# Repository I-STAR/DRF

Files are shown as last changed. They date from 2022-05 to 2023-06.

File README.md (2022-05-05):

# Open Source Library of Dynamic Reference Frames

It can be difficult to find commercially available dynamic reference frames (DRFs) for surgical tracking/navigation with a large diversity of designs permitting simultaneous tracking. As a result, many researchers resort to building their own custom-built tools. The purpose of this open-source library is to provide a variety of sets of mutually-compatible DRFs ready for 3D printing and freely available to the research community.

Please enjoy the fruits of our labor with this library of 10 sets:

- APPLE
- BANANA
- CHERRY
- DATE
- EGGFRUIT
- FIG
- GUAVA
- HONEYDEW
- JUJUBE
- KIWI

of mutually compatible dynamic reference frames (DRFs) with passive, retro-reflective markers. The APPLE set contains 10 tools, while the others contain 6. The first tool in each of the sets is the same, similar to NDI reference tool (#8700339).

The library was designed and validated at I-STAR Lab at Johns Hopkins University. All DRFs were constructed and validated using Northern Digital Inc. (NDI) geometry specifications.

# Usage Instructions

Below is a step-by-step guide to tracking DRFs with any NDI tracking system (such as Polaris Vicra or Spectra).

**STEP 1**: Download a DRF set(s) of your choosing along with the mounting post.

**STEP 2**: If you wish to modify the DRF in any way (e.g., change name, add/remove a clearance hole), use the [OpenSCAD][scad] program to open and edit the .scad file. Save by clicking “render” and then “export as STL.”

**STEP 3**: Once you have the STLs of all your desired DRFs, import them into a 3D slicing application like [Cura][cura] and print them on a 3D printer. 

**STEP 4**:  Once all the tools have been printed, attach them to the instruments you want to track using the clearance holes. Attach reflective spheres (available for purchase from NDI – and potentially other commercial sources). You can use the mounting posts as intrinsic to the CAD files, or you can order your own (metal) mounting posts from a manufacturer and attach them to the DRF. The mounting posts intrinsic to the CAD files are modeled after the NDI mounting posts (#XXX). See below for further details using built-in or separate mounting posts.

**STEP 5**: In order for the tracking system to recognize the DRF, import the tool definition file (.rom) into the tracking software. If the tracking system does not use .rom, manually create a tool definition file using the tracking system’s user guide. Manually inputting the DRF coordinates (in Coordinates section) into the tool definition file generator (e. g., 6DArchitect by NDI) will assure full compatibility of a set of DRFs.

### File Types

**STL**: This CAD file can be readily imported into any 3D printing slicing application (Cura, MakerBot Print, Slic3r, etc) and 3D printed. An .stl file can also be imported into most if not all 3D rendering software (SolidWorks, OpenSCAD, Sketchup, etc) where the DRF can be edited as well.

**SCAD**: This is an OpenSCAD file. OpenSCAD is a free software application for generating 3D computer-aided design (CAD) files. All of the available DRFs were generated using OpenSCAD. Any DRF can be modified using this program (e. g., change the DRF name, the location and sizes of the clearance holes). The posts were generated in SolidWorks and imported into OpenSCAD. For proper import, update the file location of the posts in the .scad file. 

**ROM**: This is the [tool definition file][rom] which allows any NDI tracking systems to recognize the DRF. The coordinates of the DRF is inputted manually (engineering data) in order to ensure tool compatibility. The tool definition file also specifies the origin of the tool to be at the center clearance hole. If any users require a different file type for their tool definition file or wish to specify a different origin, the coordinates for every tool are specified below under “Coordinates.”

### Modifications

If you are using a tracking system and wish to check if geometric tool specifications and compatibility are the same, please refer to the "Definitions and Tool Specifications" section.

**MOUNTING POSTS**: Currently, the DRFs are available with and without posts. The mounting posts were generated in [SolidWorks][sw] based on NDI spherical mounting posts (#XXX). The screw insertion holes for the unmounted option is non-threaded and 2 mm in diameter for NDI spherical mounting posts. The advantage of using your own mounting posts (ordered from the manufacturer) is that metal mounting posts tend to be significantly more durable than the 3D printed posts. Although not currently available, the DRF configurations are also suitable for active DRFs as well. 

**CLEARANCE HOLES**: There are three clearance holes in each DRF design. Two run through the cross body of the DRF and are 4 mm in diameter while the center clearance hole is 5 mm in diameter. The diameter can be modified in either OpenSCAD as a .scad file or in any other 3D rendering software using the .stl file. 

**ATTACHMENTS**: Custom attachments could also be added to the DRF either in 3D rendering software or physically after 3D printing using any of the available clearance holes. For the validation experiments reported in the [journal paper][manu], the tools were attached to a 3 mm diameter and 60 mm length carbon fiber rod by inserting the rod through one of the clearance holes on the cross body and securing the DRF by inserting a 10/24 set screw through the center which pushed against the rod until the attachment was stable. 

## Printing
**PRINTER**: All the validated DRFs were printed using a Lulzbot TAZ 6 but other 3D printers are also acceptable. Some families (APPLE, CHERRY, DATE, EGGFRUIT, JUJUBE) can even be printed on the Makerbot Mini which has a build plate of 100x100 mm.

**ORIENTATION**: The recommended printing orientation is flat such that the DRF has the most contact with the printer bed. The advantage of this orientation is a shorter print time with no overhang, and best quality print overall. A disadvantage is that the mounting posts are more susceptible to breaking off, but as long as the DRFs are well cared for and excessive force is not applied to the posts, they should stay intact.  

**PRINTER MATERIAL**: The two most common 3D printer filaments are ABS and PLA. [ABS has high strength and flexibility, is scratch and heat resistant, non-hygroscopic, and can be polished with acetone. Disadvantages of ABS include strong fumes during production and temperature-dependent shrinkage. ABS+ shares the same qualities as ABS but is better suited for printing large objects due to improved thermal stability. The DRFs used in this work were printed using PLA, which prints at a lower temperature and thereby minimizes shrinkage and warping. PLA+ has the qualities of PLA but is stronger, smoother, and crack resistant. Possible disadvantages of PLA are that it can become brittle when exposed to sunlight / ultraviolet light and is more reactive with water than ABS. Such effects should be negligible, if the tools are kept in a dry environment and not exposed to extended periods of direct sunlight. Overall PLA or PLA+ is recommended in order to create DRF with a minimal tracking error due to printer error.][manu]

## Definitions and Tool Specifications:

A tool length is the length between the centers of any two spheres on a DRF. Each DRF is valid in that the minimum tool length is greater than or equal to 52 mm and the differences between all tool lengths in a single DRF are larger than 5 mm. The largest tool length on any given DRF is at most 100 mm.
A tool angle is the angle between any two tool lengths on a single DRF. Similar tool lengths are two tools lengths on different DRFs which have a difference of less than 5 mm. The sets/groups available are compatible because for any pair of similar tool lengths, their angle difference is larger than 2°. 

# References
[scad] openscad.org

[cura] https://www.lulzbot.com/cura

[sw] solidworks.com

[rom] NDI 6D Architect User Guide, Northern Digital Inc. (2004).

[manu] A. Brown, A. Uneri, T. De Silva, A. Manbachi, J. H. Siewerdsen, "Design and validation of an open-source library of dynamic reference frames for research and education in optical tracking," J. Med. Imag., Special Issue on Image-Guided Procedures, Robotic Interventions, and Modeling (accepted, Sept. 2017).

## Coordinates

APPLE 01 		[-47.206 0.000], [0.345 44.316], [40.794 0.000], [-0.223 -28.594]
APPLE 02		[-56.210 0.000], [8.711 53.305], [42.291 0.000], [-3.902 -23.879]
APPLE 03		[-40.183 0.000], [4.781 51.676], [40.817 0.000], [-3.4010 -36.757]
APPLE 04		[-48.843 0.000], [1.866 50.407], [39.657 0.000], [-1.191 -32.179]
APPLE 05		[-47.289  0.000], [9.320 43.680], [46.711  0.000], [-7.017 -32.897]
APPLE 06		[-48.565  0.000], [17.490 60.390], [35.435  0.000], [-10.150 -35.047]
APPLE 07		[-46.685 0.000], [6.482 58.432], [46.815  0.000], [-3.156 -28.446]
APPLE 08		[-45.583  0.000], [19.141 50.346], [46.9171  0.000], [-16.350 -43.005]
APPLE 09		[-55.142  0.000], [-1.280 55.026], [28.358  0.000], [1.029 -44.239]
APPLE 10		[-47.253  0.000], [10.344 61.829], [45.247  0.000], [-6.106 -36.495]

BANANA 01		[-47.206 0.000], [0.345 44.316], [40.794 0.000], [-0.223 -28.594]
BANANA 02		[-47.364 0.000], [5.849 59.891], [44.636 0.000], [-5.891 -37.630]
BANANA 03		[-49.161 0.000], [5.849 66.754], [50.839 0.000], [-2.255 -25.730]
BANANA 04		[-49.267 0.000], [11.533 44.762], [50.733 0.000], [-9.107 -35.347]
BANANA 05		[-41.148 0.000], [7.134 56.736], [38.852 0.000], [-5.050 -40.161]
BANANA 06		[-53.637 0.000], [16.569 55.510], [46.363 0.000], [-6.648 -22.272]

CHERRY 01		[-47.206 0.000], [0.345 44.316], [40.794 0.000], [-0.223 -28.594]
CHERRY 02		[-48.299 0.000], [8.177 64.193], [50.700 0.000], [-3.325 -26.101]
CHERRY 03		[-45.932 0.000], [4.892 51.000], [47.568 0.000], [-3.162 -32.965]
CHERRY 04		[-54.204 0.000], [1.046 55.765], [45.796 0.000], [-0.725 -38.678]
CHERRY 05		[-48.726 0.000], [-1.422 60.756], [36.274 0.000], [0.908 -38.801]
CHERRY 06		[-52.230 0.000], [12.991 53.726], [47.770 0.000], [-5.530 -22.872]

DATE 01		[-47.206 0.000], [0.345 44.316], [40.794 0.000], [-0.223 -28.594]
DATE 02		[-42.219 0.000], [7.314 58.298], [43.281 0.000], [-4.896 -39.025]
DATE 03		[-62.726 0.000], [1.499 55.679], [28.773 0.000], [-1.177 -43.726]
DATE 04		[-49.429 0.000], [8.629 57.907], [50.571 0.000], [-5.248 -35.217]
DATE 05		[-49.935 0.000], [15.685 49.173], [50.065 0.000], [-11.359 -35.611]
DATE 06		[-53.065 0.000], [1.807 56.833], [40.935 0.000], [-0.979 -30.777]

EGGFRUIT 01	[-47.206 0.000], [0.345 44.316], [40.794 0.000], [-0.223 -28.594]
EGGFRUIT 02	[-47.287 0.000], [7.238 52.222], [49.213 0.000], [-3.992 -28.801]
EGGFRUIT 03	[-44.685 0.000], [7.858 62.954], [44.815 0.000], [-4.393 -35.197]
EGGFRUIT 04	[-55.203 0.000], [3.550 58.627], [41.797 0.000], [-1.919 -31.700]
EGGFRUIT 05	[-49.611 0.000], [16.949 50.418], [50.389 0.000], [-12.475 -37.110]
EGGFRUIT 06	[-49.340 0.000], [0.776 53.079], [41.660 0.000], [-0.470 -32.156]

FIG 01			[-47.206 0.000], [0.345 44.316], [40.794 0.000], [-0.223 -28.594]
FIG 02			[-49.976 0.000], [8.240 59.859], [50.024 0.000], [-4.036 -29.322]
FIG 03			[-49.135 0.000], [11.081 46.369], [48.365 0.000], [-7.981 -33.397]
FIG 04			[-43.086 0.000], [7.062 55.769], [41.414 0.000], [-4.400 -34.747]
FIG 05			[-59.391 0.000], [10.734 57.996], [26.109 0.000], [-7.365 -39.793]
FIG 06			[-70.717 0.000], [4.222 46.132], [29.283 0.000], [-4.326 -47.270]

GUAVA 01		[-47.206 0.000], [0.345 44.316], [40.794 0.000], [-0.223 -28.594]
GUAVA 02		[-48.219 0.000], [10.894 61.079], [51.781 0.000], [-5.626 -31.540]
GUAVA 03		[-51.467 0.000], [1.118 58.284], [42.533 0.000], [-0.796 -41.505]
GUAVA 04		[-57.834 0.000], [11.006 58.748], [42.166 0.000], [-4.504 -24.045]
GUAVA 05		[-39.422 0.000], [7.529 56.550], [39.578 0.000], [-5.214 -39.165]
GUAVA 06		[-49.745 0.000], [16.174 48.772], [50.255 0.000], [-11.786 -35.541]

HONEYDEW 01	[-47.206 0.000], [0.345 44.316], [40.794 0.000], [-0.223 -28.594]
HONEYDEW 02	[-46.624 0.000], [6.236 58.035], [45.376 0.000], [-4.256 -39.610]
HONEYDEW 03	[-55.806 0.000], [1.894 58.264], [44.194 0.000], [-1.175 -36.134]
HONEYDEW 04	[-40.249 0.000], [4.987 56.656], [40.751 0.000], [-3.738 -42.461]
HONEYDEW 05	[-58.581 0.000], [11.373 58.202], [41.419 0.000], [-4.696 -24.029]
HONEYDEW 06	[-48.507 0.000], [13.733 51.053], [51.493 0.000], [-9.138 -33.972]

JUJUBE 01		[-47.206 0.000], [0.345 44.316], [40.794 0.000], [-0.223 -28.594]
JUJUBE 02		[-49.487 0.000], [6.156 56.078], [50.513 0.000], [-3.274 -29.821]
JUJUBE 03		[-44.643 0.000], [9.278 55.667], [40.857 0.000], [-5.753 -34.519]
JUJUBE 04		[-51.564 0.000], [0.892 67.518], [40.936 0.000], [-0.427 -32.331]
JUJUBE 05		[-50.753 0.000], [-0.213 60.067], [34.747 0.000], [0.138 -38.809]
JUJUBE 06		[-46.589 0.000], [17.508 56.585], [47.411 0.000], [-12.020 -38.846]

KIWI 01		[-47.206 0.000], [0.345 44.316], [40.794 0.000], [-0.223 -28.594]
KIWI 02		[-48.249 0.000], [10.239 60.293], [42.751 0.000], [-6.300 -37.098]
KIWI 03		[-62.232 0.000], [-0.022 54.944], [29.768 0.000], [0.018 -44.466]
KIWI 04		[-48.380 0.000], [5.539 52.849], [49.120 0.000], [-3.613 -34.470]
KIWI 05		[-44.942 0.000], [0.420 59.097], [35.058 0.000], [-0.290 -40.823]
KIWI 06		[-52.797 0.000], [15.028 57.626], [47.203 0.000], [-5.808 -22.272]

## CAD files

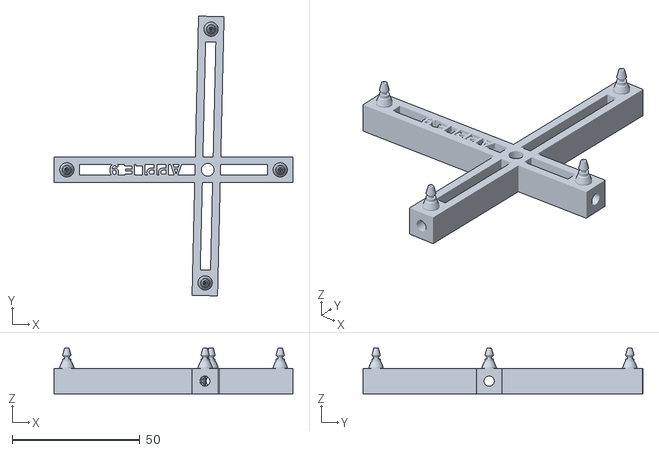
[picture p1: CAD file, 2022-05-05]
3D_Models/DRFs_with_posts/APPLE/APPLE_9_post.stl
93.5 x 109.5 x 17.9

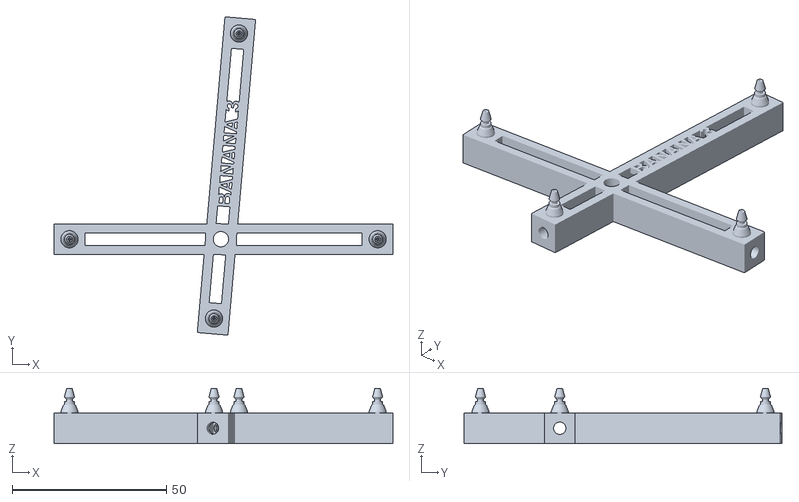
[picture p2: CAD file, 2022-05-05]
3D_Models/DRFs_with_posts/BANANA/BANANA_3_post.stl
110.0 x 103.3 x 17.9

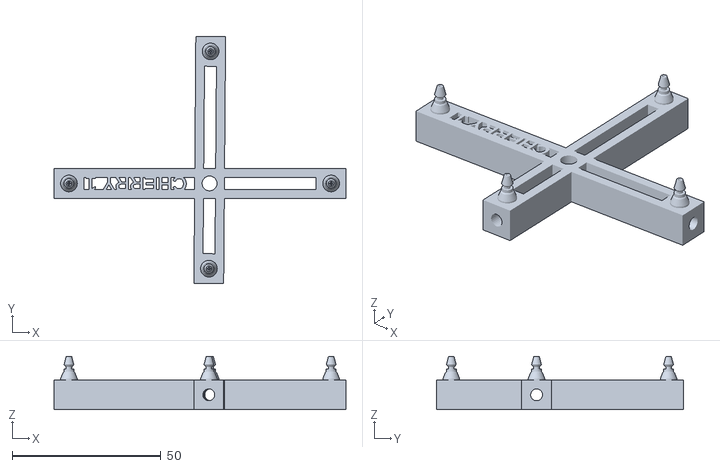
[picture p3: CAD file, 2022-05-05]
3D_Models/DRFs_with_posts/CHERRY/CHERRY_1_post.stl
98.0 x 83.0 x 17.9

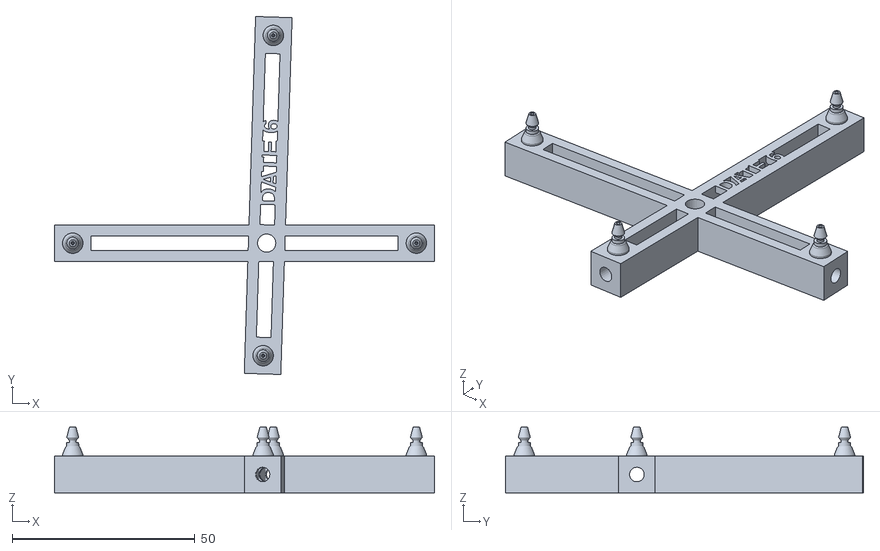
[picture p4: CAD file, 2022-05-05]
3D_Models/DRFs_with_posts/DATE/DATE_6_post.stl
104.0 x 97.9 x 17.9

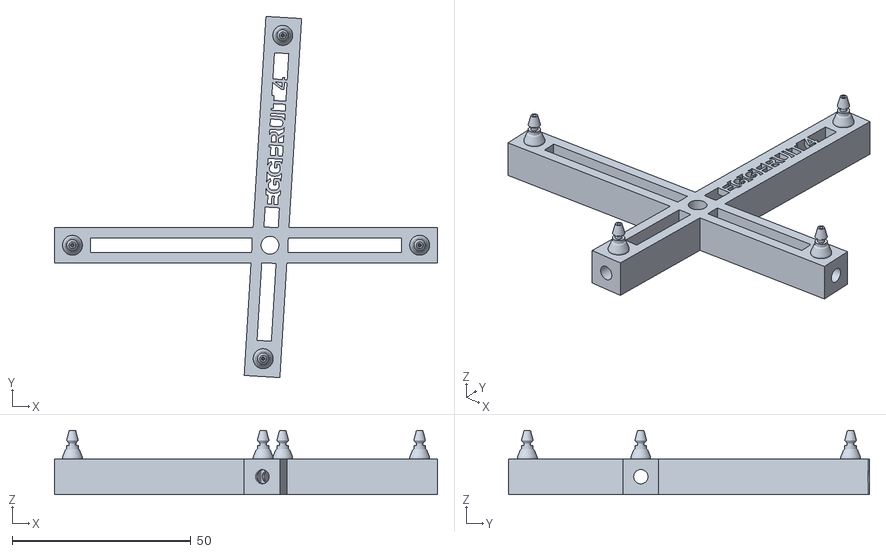
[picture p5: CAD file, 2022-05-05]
3D_Models/DRFs_with_posts/EGGFRUIT/EGGFRUIT_4_post.stl
107.0 x 100.9 x 17.9

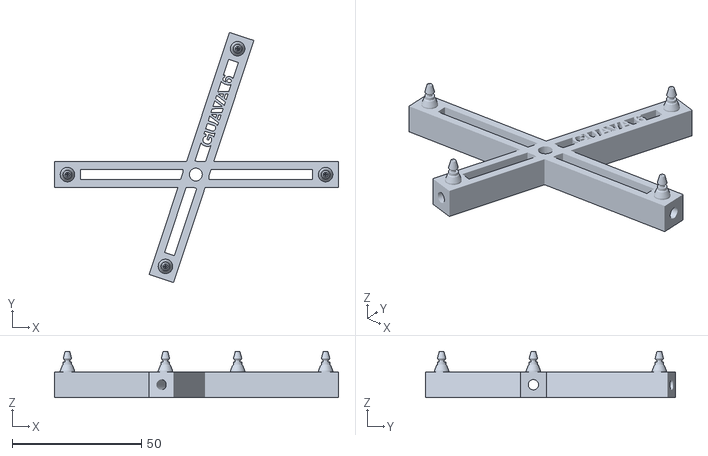
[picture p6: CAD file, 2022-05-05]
3D_Models/DRFs_with_posts/GUAVA/GUAVA_6_post.stl
110.0 x 97.0 x 17.9

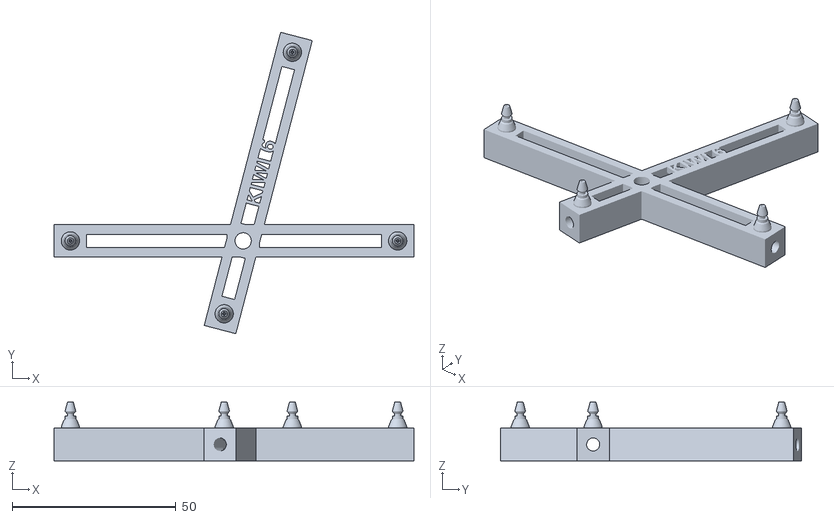
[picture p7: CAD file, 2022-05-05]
3D_Models/DRFs_with_posts/KIWI/KIWI_6_post.stl
110.0 x 92.1 x 17.9

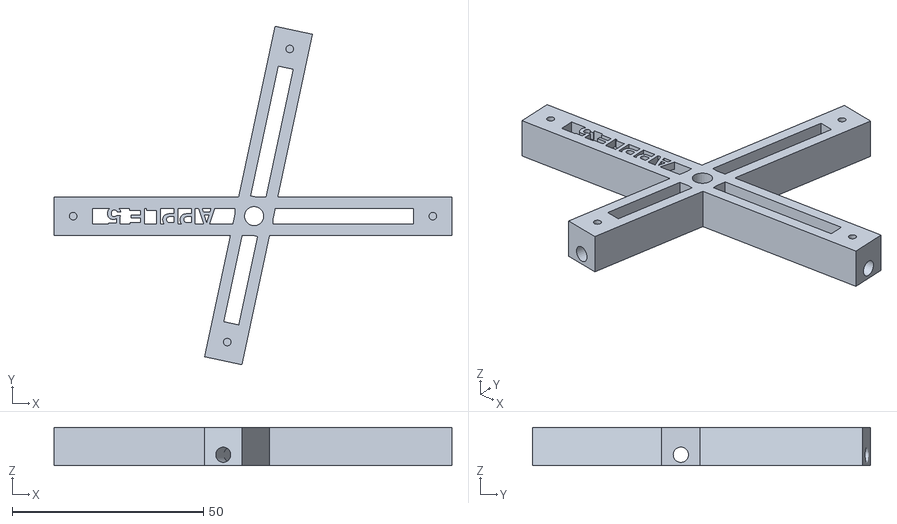
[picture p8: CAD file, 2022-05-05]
3D_Models/DRFs_without_posts/APPLE/APPLE_5_without_post.stl
104.0 x 88.4 x 10.0

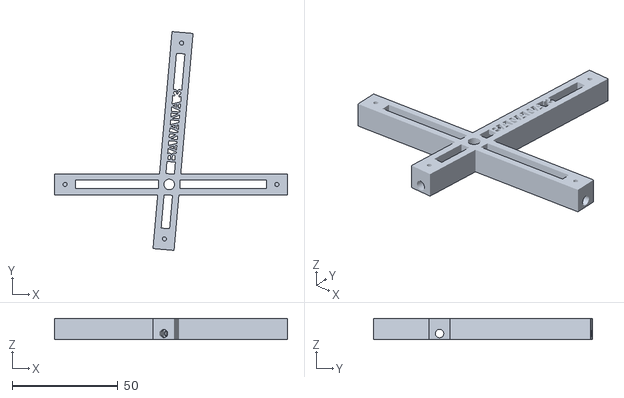
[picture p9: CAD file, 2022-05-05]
3D_Models/DRFs_without_posts/BANANA/BANANA_3_without_post.stl
110.0 x 103.3 x 10.0

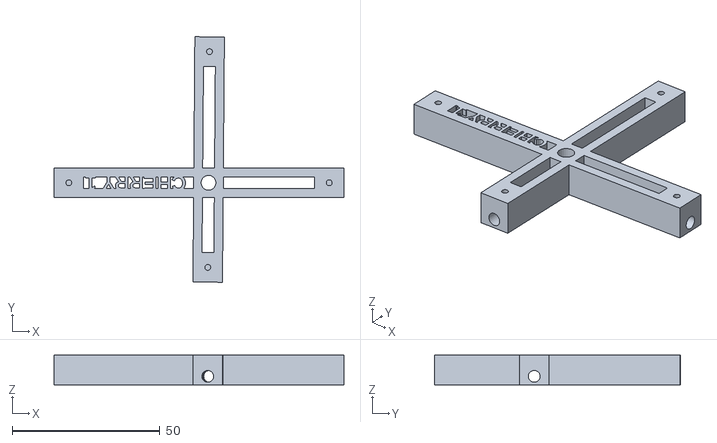
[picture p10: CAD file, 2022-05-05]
3D_Models/DRFs_without_posts/CHERRY/CHERRY_1_without_post.stl
98.0 x 83.0 x 10.0

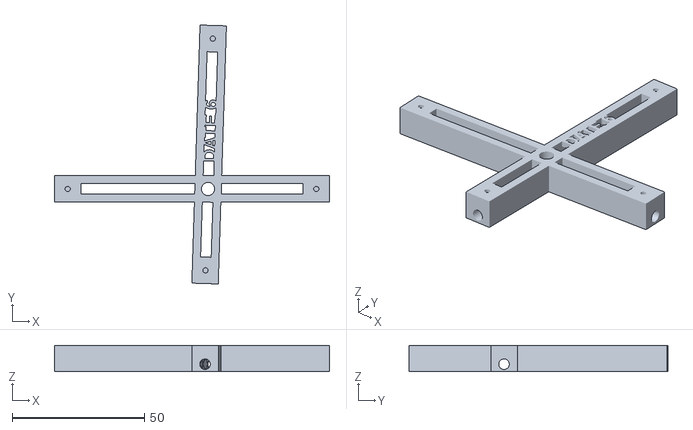
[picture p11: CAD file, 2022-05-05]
3D_Models/DRFs_without_posts/DATE/DATE_6_without_post.stl
104.0 x 97.9 x 10.0

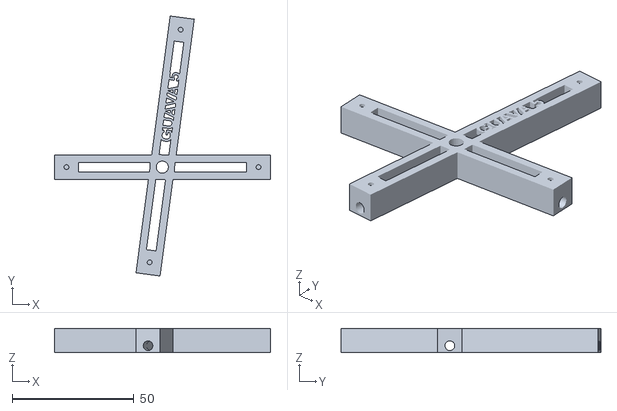
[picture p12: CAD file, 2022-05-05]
3D_Models/DRFs_without_posts/GUAVA/GUAVA_5_without_post.stl
89.0 x 106.9 x 10.0

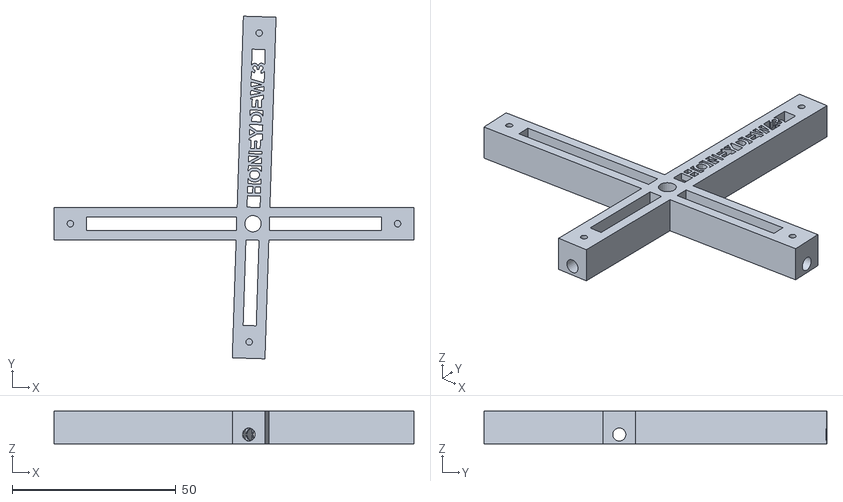
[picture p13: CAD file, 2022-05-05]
3D_Models/DRFs_without_posts/HONEYDEW/HONEYDEW_3_without_post.stl
110.0 x 104.7 x 10.0

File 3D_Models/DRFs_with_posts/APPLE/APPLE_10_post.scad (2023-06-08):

//This is rigid body contains coordinates [-47.253  0.000], [10.344 61.829], [45.247  0.000], [-6.106 -36.495]

//body of DRF parameters
dx = 92.5; //total cross length
dx1 = 45.2473; // +x direction (in blue)
dx2 = 47.2527; //-x direction (in green)
dy = 99.69; //total cross length
dy1 = 62.6882; // +y direction (in red)
dy2 = 37.0018; //-y direction (in purple)
axy = 80.5018; //angle between cross lengths

//insert file location of the mounting post
post = "C:/User/Documents/NDI_mounting_post.stl";

//clearance holes parameters
oh = 10; //central clearance hole depth
or = 2.5; //central clearance hole radius
xh = dx+10; //x-body clearance hole 1 depth
xr = 2; //x-body clearance hole 1 radius
yh = dy+10; //x-body clearance hole 2 depth
yr = xr; //x-body clearance hole 2 radius
g = 5; //z-translation of x-body clearance holes

//DRF polygon points
dx1_points_o =[[(dx1+5),5],[(dx1+5),-5],[0,-5],[0,5]];
dx2_points_o =[[-(dx2+5),5],[-(dx2+5),-5],[0,-5],[0,5]];
dy1_points_o =[[(dy1+5),5],[(dy1+5), -5],[0,-5],[0,5]];
dy2_points_o =[[(dy2+5),5],[(dy2+5), -5],[0,-5],[0,5]];
dx1_points_i =[[(dx1-5),2],[(dx1-5),-2], [(5),-2], [(5), 2]];
dx2_points_i =[[-(dx2-5),2],[-(dx2-5),-2], [-(5),-2], [-(5), 2]];
dy1_points_i =[[(dy1-5),2], [(dy1-5),-2], [5,-2], [5,2]];
dy2_points_i =[[(dy2-5),2], [(dy2-5),-2], [5,-2], [5,2]];

difference(){
    //DRF without clearance holes
    union(){
        difference(){
            color("blue")
            linear_extrude (10)
            polygon(dx1_points_o);
            linear_extrude (10)
            polygon(dx1_points_i);
        }
        color("blue")
        translate([dx1, 0, 9.9999])
        import(post);

        difference(){
            color("green")
            linear_extrude (10)
            polygon(dx2_points_o);
            linear_extrude (10)
            polygon(dx2_points_i);
        }
        color("green")
        translate([-dx2, 0, 9.9999])
        import(post);

        difference(){
            color ("red")
            rotate ([0,0,axy])
            linear_extrude (10)
            polygon(dy1_points_o);
            rotate ([0,0,axy])
            linear_extrude (10)
            polygon(dy1_points_i);
        }
        color("red")
        translate ([(cos(axy)*dy1),(sin(axy)*dy1),9.9999])
        import(post);

        difference(){
            color ("purple")
            rotate ([0,0,-(180-axy)])
            linear_extrude (10)
            polygon(dy2_points_o);
            rotate ([0,0,-(180-axy)])
            linear_extrude (10)
            polygon(dy2_points_i);
        }
        color("purple")
        translate([-(cos(axy)*dy2),-(sin(axy)*dy2),9.9999])
        import(post);
    }

    //clearance holes
    union(){
        //central clearance hole
        cylinder(oh,or,or,$fn=25);
        //x-body clearance hole 1
        rotate([0,-90,0])
        translate([g,0,-(dx1+5)])
        cylinder(xh, xr, xr, $fn=25);
        //x-body clearance hole 2
        rotate([axy,-90,0])
        translate([g,0,-(dy1+5)])
        cylinder(yh, yr, yr, $fn=25);
    }
}

translate([4,10, 8])
rotate([0,0,axy])
linear_extrude(2)
{text("APPLE 10",5, font = "Liberation Sans:style=Bold");}

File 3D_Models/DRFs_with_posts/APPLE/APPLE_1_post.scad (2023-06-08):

//This is rigid body contains coordinates [-47.206 0.000], [0.345 44.316], [40.794 0.000], [-0.223 -28.594].

//body of DRF parameters
dx = 88; //total cross length
dx1 = 40.7941; // +x direction (in blue)
dx2 = 47.2059; //-x direction (in green)
dy = 72.912; //total cross length
dy1 = 44.3171; // +y direction (in red)
dy2 = 28.5949; //-y direction (in purple)
axy = 89.5536; //angle between cross lengths

//insert file location of the mounting post
post = "C:/User/Documents/NDI_mounting_post.stl";

//clearance holes parameters
oh = 10; //central clearance hole depth
or = 2.5; //central clearance hole radius
xh = dx+10; //x-body clearance hole 1 depth
xr = 2; //x-body clearance hole 1 radius
yh = dy+10; //x-body clearance hole 2 depth
yr = xr; //x-body clearance hole 2 radius
g = 5; //z-translation of x-body clearance holes

//DRF polygon points
dx1_points_o =[[(dx1+5),5],[(dx1+5),-5],[0,-5],[0,5]];
dx2_points_o =[[-(dx2+5),5],[-(dx2+5),-5],[0,-5],[0,5]];
dy1_points_o =[[(dy1+5),5],[(dy1+5), -5],[0,-5],[0,5]];
dy2_points_o =[[(dy2+5),5],[(dy2+5), -5],[0,-5],[0,5]];
dx1_points_i =[[(dx1-5),2],[(dx1-5),-2], [(5),-2], [(5), 2]];
dx2_points_i =[[-(dx2-5),2],[-(dx2-5),-2], [-(5),-2], [-(5), 2]];
dy1_points_i =[[(dy1-5),2], [(dy1-5),-2], [5,-2], [5,2]];
dy2_points_i =[[(dy2-5),2], [(dy2-5),-2], [5,-2], [5,2]];

difference(){
    //DRF without clearance holes
    union(){
        difference(){
            color("blue")
            linear_extrude (10)
            polygon(dx1_points_o);
            linear_extrude (10)
            polygon(dx1_points_i);
        }
        color("blue")
        translate([dx1, 0, 9.9999])
        import(post);

        difference(){
            color("green")
            linear_extrude (10)
            polygon(dx2_points_o);
            linear_extrude (10)
            polygon(dx2_points_i);
        }
        color("green")
        translate([-dx2, 0, 9.9999])
        import(post);

        difference(){
            color ("red")
            rotate ([0,0,axy])
            linear_extrude (10)
            polygon(dy1_points_o);
            rotate ([0,0,axy])
            linear_extrude (10)
            polygon(dy1_points_i);
        }
        color("red")
        translate ([(cos(axy)*dy1),(sin(axy)*dy1),9.9999])
        import(post);

        difference(){
            color ("purple")
            rotate ([0,0,-(180-axy)])
            linear_extrude (10)
            polygon(dy2_points_o);
            rotate ([0,0,-(180-axy)])
            linear_extrude (10)
            polygon(dy2_points_i);
        }
        color("purple")
        translate([-(cos(axy)*dy2),-(sin(axy)*dy2),9.9999])
        import(post);
    }

    //clearance holes
    union(){
        //central clearance hole
        cylinder(oh,or,or,$fn=25);
        //x-body clearance hole 1
        rotate([0,-90,0])
        translate([g,0,-(dx1+5)])
        cylinder(xh, xr, xr, $fn=25);
        //x-body clearance hole 2
        rotate([axy,-90,0])
        translate([g,0,-(dy1+5)])
        cylinder(yh, yr, yr, $fn=25);
    }
}

translate([-10,2.3, 8])
rotate([0,0,180])
linear_extrude(2)
{text("APPLE 1",5, font = "Liberation Sans:style=Bold");}

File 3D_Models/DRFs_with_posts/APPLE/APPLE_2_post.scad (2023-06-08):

//This is rigid body contains coordinates [-56.210 0.000], [8.711 53.305], [42.291 0.000], [-3.902 -23.879]

//body of DRF parameters
dx = 98.5; //total cross length
dx1 = 42.2895; // +x direction (in blue)
dx2 = 56.2105; //-x direction (in green)
dy = 78.21; //total cross length
dy1 = 54.0115; // +y direction (in red)
dy2 = 24.1985; //-y direction (in purple)
axy = 80.7204; //angle between cross lengths

//insert file location of the mounting post
post = "C:/User/Documents/NDI_mounting_post.stl";

//clearance holes parameters
oh = 10; //central clearance hole depth
or = 2.5; //central clearance hole radius
xh = dx+10; //x-body clearance hole 1 depth
xr = 2; //x-body clearance hole 1 radius
yh = dy+10; //x-body clearance hole 2 depth
yr = xr; //x-body clearance hole 2 radius
g = 5; //z-translation of x-body clearance holes

//DRF polygon points
dx1_points_o =[[(dx1+5),5],[(dx1+5),-5],[0,-5],[0,5]];
dx2_points_o =[[-(dx2+5),5],[-(dx2+5),-5],[0,-5],[0,5]];
dy1_points_o =[[(dy1+5),5],[(dy1+5), -5],[0,-5],[0,5]];
dy2_points_o =[[(dy2+5),5],[(dy2+5), -5],[0,-5],[0,5]];
dx1_points_i =[[(dx1-5),2],[(dx1-5),-2], [(5),-2], [(5), 2]];
dx2_points_i =[[-(dx2-5),2],[-(dx2-5),-2], [-(5),-2], [-(5), 2]];
dy1_points_i =[[(dy1-5),2], [(dy1-5),-2], [5,-2], [5,2]];
dy2_points_i =[[(dy2-5),2], [(dy2-5),-2], [5,-2], [5,2]];

difference(){
    //DRF without clearance holes
    union(){
        difference(){
            color("blue")
            linear_extrude (10)
            polygon(dx1_points_o);
            linear_extrude (10)
            polygon(dx1_points_i);
        }
        color("blue")
        translate([dx1, 0, 9.9999])
        import(post);

        difference(){
            color("green")
            linear_extrude (10)
            polygon(dx2_points_o);
            linear_extrude (10)
            polygon(dx2_points_i);
        }
        color("green")
        translate([-dx2, 0, 9.9999])
        import(post);

        difference(){
            color ("red")
            rotate ([0,0,axy])
            linear_extrude (10)
            polygon(dy1_points_o);
            rotate ([0,0,axy])
            linear_extrude (10)
            polygon(dy1_points_i);
        }
        color("red")
        translate ([(cos(axy)*dy1),(sin(axy)*dy1),9.9999])
        import(post);

        difference(){
            color ("purple")
            rotate ([0,0,-(180-axy)])
            linear_extrude (10)
            polygon(dy2_points_o);
            rotate ([0,0,-(180-axy)])
            linear_extrude (10)
            polygon(dy2_points_i);
        }
        color("purple")
        translate([-(cos(axy)*dy2),-(sin(axy)*dy2),9.9999])
        import(post);
    }

    //clearance holes
    union(){
        //central clearance hole
        cylinder(oh,or,or,$fn=25);
        //x-body clearance hole 1
        rotate([0,-90,0])
        translate([g,0,-(dx1+5)])
        cylinder(xh, xr, xr, $fn=25);
        //x-body clearance hole 2
        rotate([axy,-90,0])
        translate([g,0,-(dy1+5)])
        cylinder(yh, yr, yr, $fn=25);
    }
}

translate([-10,2.4, 8])
rotate([0,0,180])
linear_extrude(2)
{text("APPLE 2",5, font = "Liberation Sans:style=Bold");}

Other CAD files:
3D_Models/DRFs_with_posts/FIG/FIG_6_post.stl
3D_Models/DRFs_with_posts/HONEYDEW/HONEYDEW_5_post.stl
3D_Models/DRFs_with_posts/JUJUBE/JUJUBE_2_post.stl
3D_Models/DRFs_without_posts/EGGFRUIT/EGGFRUIT_5_without_post.stl
3D_Models/DRFs_without_posts/FIG/FIG_6_without_post.stl
3D_Models/DRFs_with_posts/APPLE/APPLE_3_post.scad
3D_Models/DRFs_with_posts/APPLE/APPLE_10_post.stl
3D_Models/DRFs_with_posts/APPLE/APPLE_1_post.stl
3D_Models/DRFs_with_posts/APPLE/APPLE_2_post.stl
3D_Models/DRFs_with_posts/APPLE/APPLE_3_post.stl
3D_Models/DRFs_with_posts/APPLE/APPLE_4_post.scad
3D_Models/DRFs_with_posts/APPLE/APPLE_4_post.stl
3D_Models/DRFs_with_posts/APPLE/APPLE_5_post.scad
3D_Models/DRFs_with_posts/APPLE/APPLE_5_post.stl
3D_Models/DRFs_with_posts/APPLE/APPLE_6_post.scad
3D_Models/DRFs_with_posts/APPLE/APPLE_6_post.stl
3D_Models/DRFs_with_posts/APPLE/APPLE_7_post.scad
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

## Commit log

2022-05-05 Move from I-STAR downloads page, part 2
    [APPLE_10_post.scad, APPLE_10_post.stl, APPLE_10_without_post.scad, APPLE_10_without_post.stl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]
2022-05-05 Upload marker sets
    [BANANA_1_post.scad, BANANA_1_post.stl, BANANA_2_post.scad, BANANA_2_post.stl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]
2022-05-05 Upload marker sets without posts
    [BANANA_1_without_post.scad, BANANA_1_without_post.stl, BANANA_2_without_post.scad, BANANA_2_without_post.stl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]
2023-04-20 Compatible with FreeCAD
    [APPLE_10_post.scad, APPLE_10_without_post.scad, APPLE_1_post.scad, APPLE_1_without_post.scad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]
